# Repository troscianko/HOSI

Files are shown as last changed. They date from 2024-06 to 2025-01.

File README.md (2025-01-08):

# HOSI: Hyperspectral open source imager

_Developed by Jolyon Troscianko_

The hyperspectral open-source imaging system (HOSI) is an innovative and low-cost solution for collecting full-field hyperspectral data. The system uses a Hamamatsu C12880MA micro spectrometer to take single-point measurements, together with a motorised gimbal for spatial control. The hardware uses off-the-shelf components and 3D printed parts, costing around £350 in total. The system can run directly from a computer or smartphone with a graphical user interface, making it highly portable and user-friendly.

The HOSI system can take panoramic hyperspectral images that meet the difficult requirements of ALAN research, sensitive to low light around 0.001 cd.m-2, across 320-880nm range with spectral resolution of ~9nm (FWHM) and spatial resolution of ~0.2 degrees. The independent exposure of each pixel also allows for an extremely wide dynamic range that can encompass typical natural and artificially illuminated scenes, with sample night-time scans achieving peak-to-peak dynamic ranges of >50,000:1.

This system's adaptability, cost-effectiveness, and open-source nature position it as a valuable tool for researchers investigating the complex relationships between light, environment, behaviour, ecology, and biodiversity, with further potential uses in many other fields.

# Publicaiton:
For further information, including detailed performance data, see my paper:

**Troscianko, J.** A hyperspectral open-source imager (HOSI). _BMC Biol_ 23, 5 (2025). https://doi.org/10.1186/s12915-024-02110-w

Please cite the above paper if you use this project :)

# Videos:
Intro video (https://www.youtube.com/watch?v=9q8lyUpntms)
Assembly video (https://www.youtube.com/watch?v=4VSr_2GacWA)
Firmware video (https://www.youtube.com/watch?v=N6yWZMLm-1M)
Calibration video (https://www.youtube.com/watch?v=MEW3B65dHIc)
Imaging video (https://www.youtube.com/watch?v=LO7XNOPuY0w)

# Figures:

wiring and 3D parts
_Figure 1. 3D parts and wiring. a) Photograph of a HOSI unit in the field, running from a smartphone. b): 3D assembly; c): parts arranged for 3D printing; d): wiring diagram and required wire lengths. GND (ground) is the shared negative voltage, VIN is the 5v output from the Arduino that is delivered via the USB cable. Note that the spectrometer should be connected to the Arduino’s regulated 5v output (as shown), not VIN that has a slightly lower voltage due to a protective diode in the Arduino._

GUI2
_Figure 2. Graphical user interface (GUI) layout, showing the available functions and a scan of butterflies. The spectrum shows a selection from a patch of wing that appears black to human vision, but has a UV peak visible to many other animals. This scene was illuminated by an Exo-Terra Sunray lamp._


_Figure 3. Example hyperspectral scan of Falmouth (UK) docks at night. a): panoramic photograph of the scene; b): HOSI’s hyperspectral RGB preview image; c): radiance plots created by the HOSI GUI at chosen pixels (x-axis: wavelength [nm]; y-axis: linear radiance Le [W.sr-1.m-2.nm-1]). These spectra illustrate how individual light sources can be identified and compared. The highest spectral peak in the brightest pixel of this hyperspectral image is approximately 50,000 times higher than the peak in the darkest pixel. The full dynamic range (highest peak to lowest trough) is considerably greater, and can be maximised further with longer exposure times to reduce noise._

**Description of HOSI file output format** (each scan generates a .csv file and .png image):
_First line:_

'h' denotes start of raw data from HOSI, unit #, pan left limit, pan right limit, pan resolution steps-per-scan, tilt lower limit, tilt upper limit, tilt resolution (steps-per-scan), maximum integration time (microseconds), boxcar spectral pooling value, delay between dark measurement repeats (milliseconds)

_Second line onwards:_

pan location (steps), tilt location (steps), measurement type (0=dark measurement, 1=light measurement, 2=initialisation exposure), integration time (microseconds), number of wavelength bins reaching saturation point, spectral count data (288 comma-delineated measurements unless a boxcar>1 is used)

'x' denotes end of raw data

Following this, a table of processed, calibrated _Le_ values are shown, together with wavelengths, and pan/tilt locations. Note that this table uses the calibration data present when the raw file was generated.

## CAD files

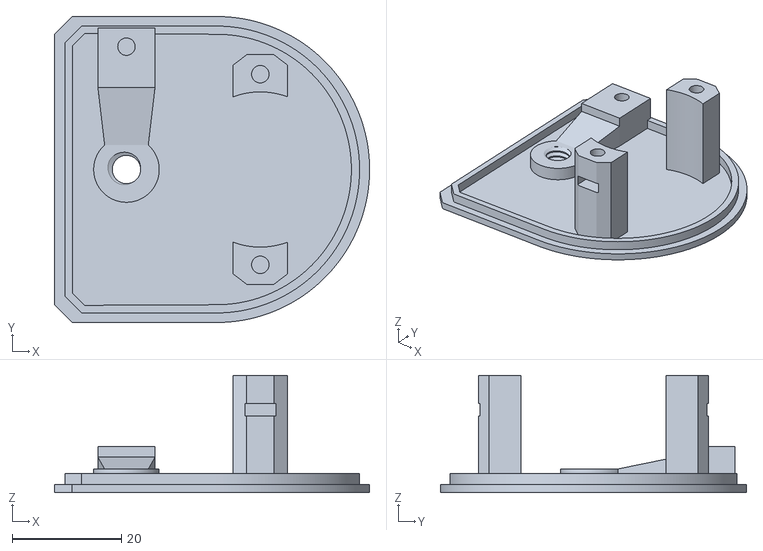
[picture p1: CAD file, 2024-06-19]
3D Models/Base B.stl
57.7 x 56.0 x 21.5

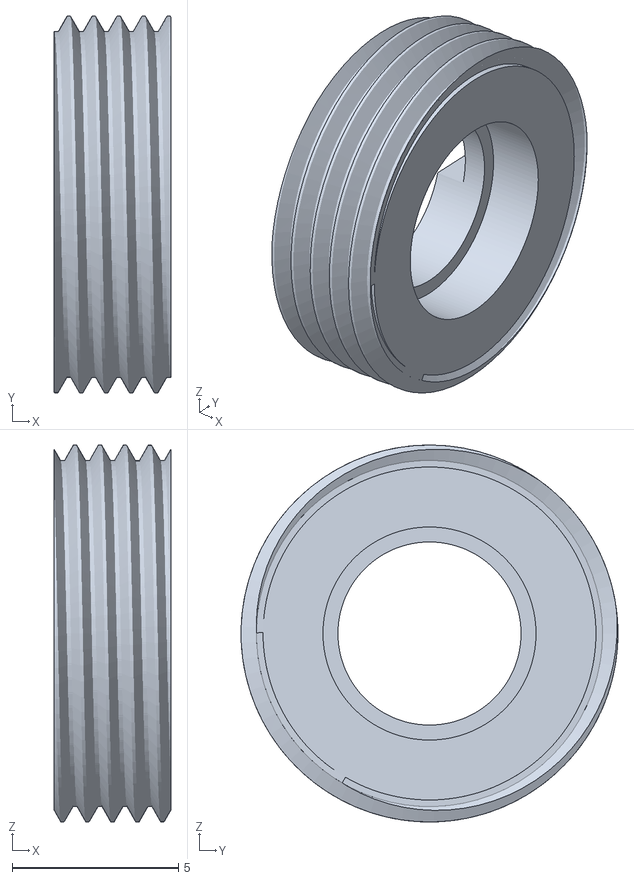
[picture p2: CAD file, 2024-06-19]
3D Models/Lens holder.stl
3.50 x 11.3 x 11.3

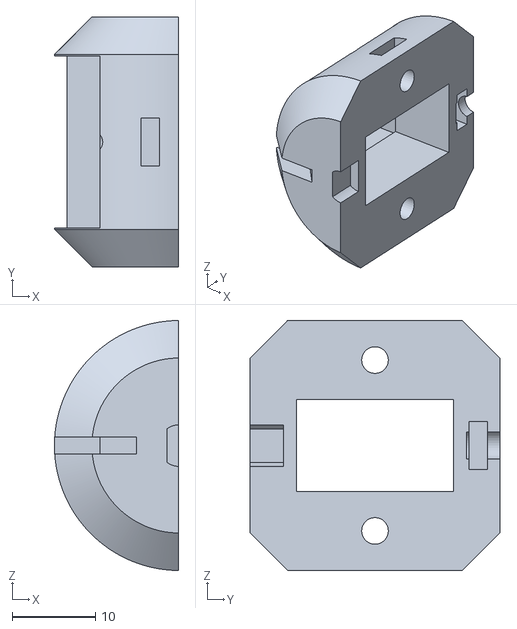
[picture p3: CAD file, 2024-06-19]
3D Models/Tilt B.stl
14.9 x 30.0 x 30.0

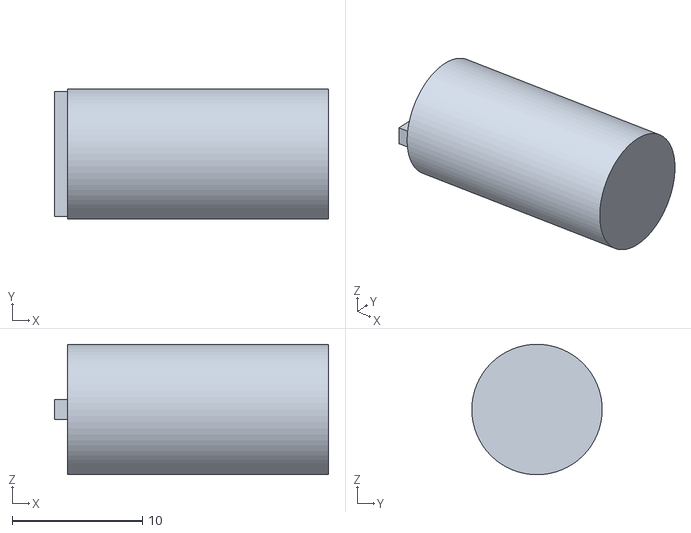
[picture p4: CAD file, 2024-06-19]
3D Models/Focus tool.stl
21.0 x 10.0 x 10.0

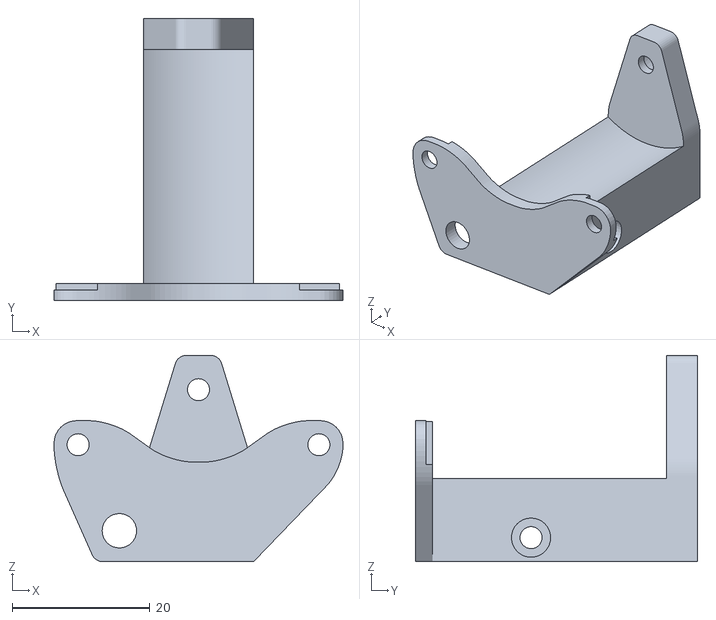
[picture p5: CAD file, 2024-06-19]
3D Models/Pan bracket.stl
42.0 x 41.0 x 30.0

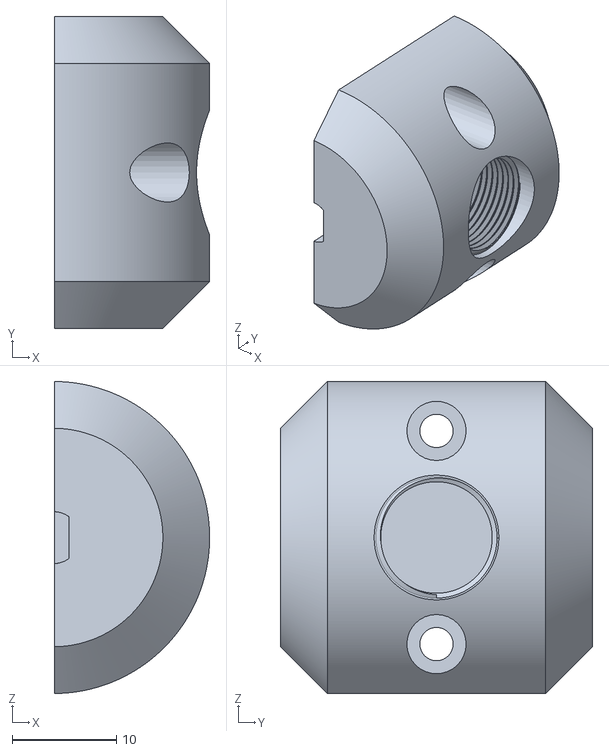
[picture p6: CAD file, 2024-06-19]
3D Models/Tilt A.stl
14.9 x 30.0 x 30.0

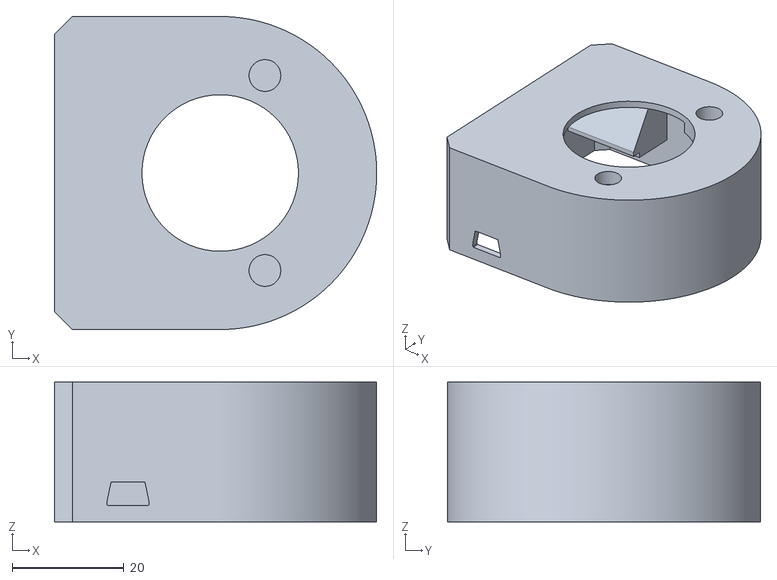
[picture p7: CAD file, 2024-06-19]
3D Models/Base A.stl
57.7 x 56.0 x 25.0

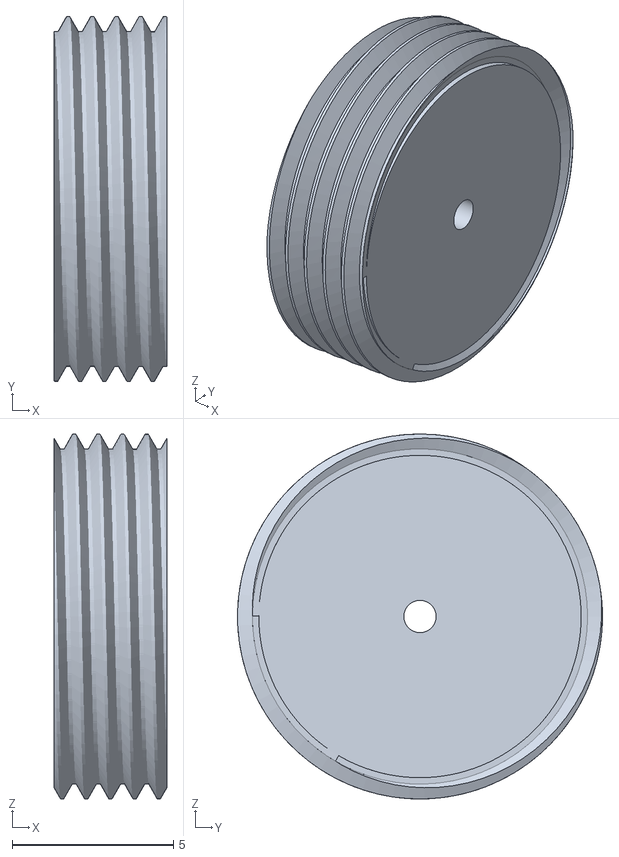
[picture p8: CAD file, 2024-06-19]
3D Models/Light reducer 1mm.stl
3.50 x 11.3 x 11.3

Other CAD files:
3D Models/Light reducer 2mm.stl

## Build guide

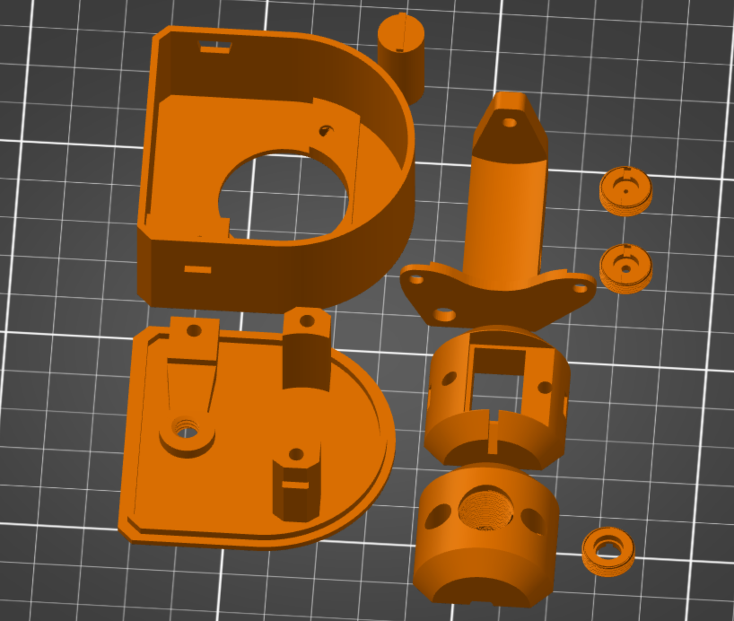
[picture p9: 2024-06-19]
3D Models/Print orientations.png

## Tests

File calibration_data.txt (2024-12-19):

unit,data,
9,wavCoef,3.150073901E+02,2.700335692E+00,-1.370721454E-03,-5.494487172E-06,1.475143134E-09,1.441646208E-11,
9,radSens,10.57054,10.31393,9.96353,9.75570,9.90073,10.52882,11.67749,13.29625,15.25959,17.38610,19.46953,21.31691,22.78413,23.79880,24.36451,24.54783,24.45461,24.20453,23.90981,23.66150,23.52308,23.53039,23.69609,24.01660,24.47917,25.06546,25.75057,26.49864,27.25994,27.97367,28.57747,29.02001,29.27114,29.32534,29.19893,28.92344,28.53918,28.08971,27.61815,27.16415,26.76176,26.43859,26.21611,26.11092,26.13597,26.30099,26.61160,27.06730,27.66013,28.37490,29.19203,30.09118,31.05243,32.05223,33.05475,34.00388,34.82338,35.42944,35.75312,35.76313,35.47760,34.95881,34.29317,33.56562,32.83927,32.14679,31.49384,30.87027,30.26316,29.66717,29.08916,28.54665,28.06171,27.65326,27.33167,27.09737,26.94303,26.85745,26.82873,26.84534,26.89544,26.96527,27.03859,27.09778,27.12658,27.11312,27.05206,26.94520,26.80059,26.63053,26.44892,26.26822,26.09717,25.93981,25.79622,25.66434,25.54181,25.42684,25.31836,25.21585,25.11898,25.02774,24.94233,24.86304,24.78973,24.72115,24.65448,24.58571,24.51068,24.42651,24.33254,24.23028,24.12271,24.01346,23.90639,23.80552,23.71480,23.63732,23.57414,23.52325,23.47947,23.43524,23.38199,23.31145,23.21658,23.09247,22.93664,22.74920,22.53245,22.29057,22.02964,21.75775,21.48440,21.21869,20.96663,20.72914,20.50203,20.27826,20.05127,19.81782,19.57902,19.33942,19.10503,18.88135,18.67205,18.47842,18.29935,18.13191,17.97274,17.81980,17.67365,17.53706,17.41271,17.30013,17.19391,17.08403,16.95850,16.80697,16.62389,16.41045,16.17463,15.92983,15.69204,15.47680,15.29626,15.15735,15.06100,15.00240,14.97182,14.95597,14.93989,14.90964,14.85537,14.77440,14.67273,14.56386,14.46429,14.38725,14.33748,14.30931,14.28929,14.26120,14.21113,14.13064,14.01787,13.87669,13.71445,13.53934,13.35800,13.17552,12.99744,12.83223,12.69203,12.59003,12.53552,12.52887,12.55890,12.60349,12.63355,12.61860,12.53263,12.35920,12.09501,11.75136,11.35251,10.93063,10.51851,10.14253,9.81825,9.54977,9.33226,9.15557,9.00737,8.87521,8.74718,8.61231,8.46099,8.28568,8.08207,7.84967,7.59159,7.31309,7.01973,6.71651,6.40891,6.10583,5.82341,5.58792,5.43539,5.40608,5.53381,5.83285,6.28837,6.85490,7.46404,8.03821,8.50524,8.80975,8.91932,8.82560,8.54190,8.09844,7.53661,6.90294,6.24326,5.59761,4.99634,4.45827,3.99102,3.59353,3.25990,2.98304,2.75728,2.57912,2.44651,2.35739,2.30877,2.29604,2.31302,2.35209,2.40473,2.46246,2.51802,2.56604,2.60216,2.62187,2.61994,2.59173,2.53572,2.45605,2.36296,2.27099,2.19597,2.15221,2.15024,2.19468,2.28250,2.40223,2.53538,2.65999,2.75539,2.80680,2.80867,2.76586,2.69257,2.60923,2.53784,2.49689,
9,linCoefs,0.91106809,0.58315014,

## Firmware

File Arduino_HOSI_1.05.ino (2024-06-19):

/*

_________________________HOSI Arduino Firmware_____________________________

 Written by: Jolyon Troscianko
 initial release: 19/06/2024
 License: GNU General Public License v3.0
 
 
 Manual control:
 The HOSI can be controlled automatically by the HOSI_GUI Python software. however, the functions can
 also be accessed manually via a serial port (check the baud, default 115200)
 
 tilt: send "l" followed by a number e.g. "l100" or "l500" note that zero is straight down, do not use negative values
 pan: send "p" followed by a number e.g. "p100" or "p-1000" note that zero is straight ahead
 manual integration time: send "t" followed by microsecond number
 radiance measurement: send "r" and it will take a radiance measurement
 hyperspectral measurement: send "h" followed by comma-delineated values as follows:
 panLeft,panRight,panResolution,tiltBottom,tiltTop,tiltResolution,maxIntegrationTime(microseconds),boxcar,darkRepeatTimer(milliseconds)
 e.g.: "h-200,200,10,400,600,10,2000000,2,120000"
  
 
 Modify the unit number below if desired, and upload this script to an Arduino Nano or similar.
 
 
 */


#include <AccelStepper.h>




int unitNumber = 9; // Change this number to whatever you want, and link this to the calibration data in calibration_data.txt


#define TRGpin A0
#define STpin A1
#define CLKpin A2
#define VIDEOpin A3

#define nSites 288 // 
uint16_t data[nSites] [2];
int dataLoc = 0;

int delayTime = 1;
long intTime = 100;
long prevIntTime = 100;
long maxIntTime = 3000000; // maximum integration time for auto & manual measurement milliseconds
int minIntTime = 50; //the sensor doesn't work below a certain numebr of scans... it needs three cycles with the ST pin high, even then you need to add about 378 microseconds to the exposure
int intStep = 400;
long manIntTime = 0;
int satN = 0; // number of bands over-exposed
int prevSatN = 0;
int satVal = 998; // over-exposure value

// used to control the reduction of redundant measurements at high elevations
int panoSteps[] = {913, 959, 988, 1005};
int panoSpaces[] = {2, 4, 8, 16};

long hyperVals[9];
long panVal = 0;
long tiltVal = 0;
int darkLight = 1; // 0= dark measurement, 1=light measurement
long darkRepeat = 30000;// repeat dark measurement every few seconds/minutes

AccelStepper stepper_pan(4, 3, 5, 2, 4); // 8=HALF4WIRE, then input pin 1, 2, 3, 4
AccelStepper stepper_tilt(4, 7, 9, 6, 8); // 8=HALF4WIRE, then input pin 1, 2, 3, 4

int boxcar = 1;



void setup() {
  stepper_pan.setMaxSpeed(500.0); // 800 for half-step
  stepper_pan.setAcceleration(5000.0);
  stepper_pan.disableOutputs();

  stepper_tilt.setMaxSpeed(500.0);
  stepper_tilt.setAcceleration(5000.0);  
  stepper_tilt.disableOutputs();
      
  //Set desired pins to OUTPUT
  pinMode(CLKpin, OUTPUT);
  pinMode(STpin, OUTPUT);

  digitalWrite(CLKpin, HIGH);
  digitalWrite(STpin, LOW);

  Serial.begin(115200); // Baud Rate set to 115200, 500000 seems to work well for nano with PC, 230400 and 256000 doesn't work for android. interestingly it still works ok with 57600
  while (! Serial); // Wait untilSerial is ready
  readSpectrometer();
  resetData();
  
}




void readSpectrometer(){

  // Start clock cycle and set start pulse to signal start
  digitalWrite(CLKpin, LOW);
  delayMicroseconds(delayTime);
  digitalWrite(CLKpin, HIGH);
  delayMicroseconds(delayTime);
  digitalWrite(CLKpin, LOW);
  digitalWrite(STpin, HIGH);
  delayMicroseconds(delayTime);

  // microseconds
     unsigned long cTime = micros(); // start time
     unsigned long eTime = cTime + intTime; // end time
  
  //Sample for a period of time
 // for(int i = 0; i < 15; i++){ //orig 15
     while(cTime < eTime){
         digitalWrite(CLKpin, HIGH);
         delayMicroseconds(delayTime);
         digitalWrite(CLKpin, LOW);
         delayMicroseconds(delayTime);
         cTime=micros();
      } 

  //Set STpin to low
  digitalWrite(STpin, LOW);

  //Sample for a period of time
  for(int i = 0; i < 88; i++){ //87 aligns correctly

      digitalWrite(CLKpin, HIGH);
      delayMicroseconds(delayTime);
      digitalWrite(CLKpin, LOW);
      delayMicroseconds(delayTime); 
      
  }

  int specRead = 0;
  satN = 0;
  for(int i = 0; i < nSites; i++){

      specRead = analogRead(VIDEOpin);
      // second read shoudl stablise the multiplexer and give more accurate read
      //delayMicroseconds(delayTime);
     // specRead = analogRead(VIDEOpin);
      data[i][dataLoc] += specRead;
      if(specRead > satVal)
        satN ++;
      
      digitalWrite(CLKpin, HIGH);
      delayMicroseconds(delayTime);
      digitalWrite(CLKpin, LOW);
      delayMicroseconds(delayTime);
        
  } 
}



void resetData(){
  for (int i = 0; i < nSites; i++)
    data[i][dataLoc] = 0;
}

void switchDim(){
  if(dataLoc == 0)
    dataLoc = 1;
  else
    dataLoc = 0;
}

void radianceMeasure(){

  // reset all data
  dataLoc = 1;
  resetData();
  dataLoc = 0;
  resetData();

  // ----------------- AUTO EXPOSURE-----------
  if(manIntTime == 0){ 
    intTime = minIntTime; // microsecond exposure
    readSpectrometer(); // read to dim0
    //data[0][dataLoc] = -1; // debugging
    prevSatN = satN;
    prevIntTime = intTime;
    intTime = intStep;
    if(satN > 0)
      switchDim(); // required if first exposure is over-exposed

    while(satN == 0 && intTime < maxIntTime){
      switchDim();
      resetData();
      readSpectrometer();
      //data[0][dataLoc] = intTime;// debugging

      if(satN == 0){
        prevSatN = satN;
        prevIntTime = intTime;
        intTime = intTime*2;
      }

    } //while

    //if(prevIntTime > -1) // if first exposure isn't over-exposed
      switchDim(); 
      
  //------------- MANUAL EXPOSURE-------------
  } else { 
    intTime = manIntTime;
    readSpectrometer(); // read to dim0
    prevSatN = satN;
    prevIntTime = intTime;
  }
 
  Serial.print(String(panVal) + "," + String(tiltVal) + "," + String(darkLight) + "," + String(prevIntTime) + "," + String(prevSatN) );

  for (int i = 0; i < nSites; i+=boxcar){
    int tSum = 0;
    for(int j = 0; j < boxcar; j++)
      if(i+j <= nSites)
          tSum += data[i+j][dataLoc];
    Serial.print("," + String(tSum));
  }
  Serial.print("\n");
  delay(1);
 
}


void pan(long pv){
  //stepper_pan.enableOutputs();
  stepper_pan.runToNewPosition(pv);
  //stepper_pan.disableOutputs();
}

void tilt(long tv){
  //stepper_tilt.enableOutputs();
  stepper_tilt.runToNewPosition(tv);
  //stepper_tilt.disableOutputs();
}

void darkMeasure(){
      //-----------Return to zero point------------
      //panVal = 0;
      //pan(0);
      //tiltVal = 0;
      tilt(0);
      darkLight = 0; // dark measurement
      long tl = manIntTime; // save existing manual value

      // first scan at microsecond
      manIntTime = minIntTime;
      radianceMeasure();
   
      for (long i = intStep; i <= maxIntTime; i*= 2){
        manIntTime = i;
        radianceMeasure();
      }

      manIntTime = tl;// restore manIntTime
      darkLight = 1; // light measurement
}

void startMeasure(){
      //-----------Return to zero point------------
      //panVal = 0;
      pan(0);
      //tiltVal = 512;
      tilt(512);
      darkLight = 2; // dark measurement
      radianceMeasure();
      darkLight = 1; // light measurement
}


void loop() {

  
  String arg = Serial.readString();

  if (arg != NULL){

    // manually set integration time
    if(arg.startsWith("t") == true){
      arg.replace("t", "");
      manIntTime = (long) arg.toFloat();
      if(manIntTime > maxIntTime)
          manIntTime = maxIntTime;
      Serial.println("int. time: " + String(manIntTime) + "ms");

    // manual pan
    } else if(arg.startsWith("p") == true){
      arg.replace("p", "");
      stepper_pan.enableOutputs();
      pan((int) arg.toFloat());
      stepper_pan.disableOutputs();
      Serial.println("pan: " + String((int) arg.toFloat()));
      delay(5);

    // manual tilt
    } else if(arg.startsWith("l") == true){
      arg.replace("l", "");
      stepper_tilt.enableOutputs();
      tilt((int) arg.toFloat());
      stepper_tilt.disableOutputs();
      Serial.println("tilt: " + String((int) arg.toFloat()));
      delay(5);

    // Manual spec measure
    } else if(arg.startsWith("r") == true){ // radiance

      radianceMeasure();

    // -------------  hyperspec --------------
    } else if(arg.startsWith("h") == true){
      arg.replace("h", "");
      int i= 0;
      while(arg.indexOf(",") != -1){
        hyperVals[i] = long(arg.substring(0,arg.indexOf(",")).toFloat()); //toInt for int, atol for long
        i++;
        arg = arg.substring(arg.indexOf(",")+1);
      }

   

      Serial.println("h," + String(unitNumber) + "," + String(hyperVals[0]) + "," + String(hyperVals[1]) + "," + String(hyperVals[2]) + "," + String(hyperVals[3]) + "," + String(hyperVals[4]) + "," + String(hyperVals[5]) + "," + String(hyperVals[6]) + "," + String(hyperVals[7]) + "," + String(hyperVals[8]) );
      delay(5);
      //arg = Serial.readString();
      
      maxIntTime = (long) hyperVals[6];
      boxcar = (int) hyperVals[7];
      darkRepeat = (long) hyperVals[8];

      stepper_pan.enableOutputs();
      stepper_tilt.enableOutputs();
      //panVal = 0;
      pan(0);
      tilt(0);

      //-----------Dark Measure at start------------
      startMeasure();
      darkMeasure();

      unsigned long cDR = millis(); // current time dark repeat
      unsigned long eDR = cDR + darkRepeat; // end time dark repeat
      
      for(tiltVal = hyperVals[3]; tiltVal <= hyperVals[4]; tiltVal += hyperVals[5]){
        
        //----------repeat dark measurement based on timeout-----------
        cDR = millis();
        if(cDR >= eDR){
            darkMeasure();
            //tilt(tiltVal);
            cDR = millis();
            eDR = cDR + darkRepeat;
        }

        tilt(tiltVal);
        pan(hyperVals[0]-10);// overshoot - pan left a bit to use up excess in gears

        //--------reduce measurement frequency at high elevations
        int panShift = 1;
        int panStart = 0;
        for(int i=0; i<4; i++)
        if(tiltVal >= panoSteps[i]){
            panShift = panoSpaces[i];
            panStart = panoSpaces[i]/2;
        }
        panShift *= hyperVals[2];
        panStart *= hyperVals[2];
            
        /*
        if(panVal >= hyperVals[1]){
          //----------pan from right to left-----------
          for(panVal = hyperVals[1]-panStart; panVal >= hyperVals[0]; panVal -= panShift){ 
            pan(panVal);
            radianceMeasure();
          }
        } else {
        */
          //----------pan from left to right-----------
          for(panVal = hyperVals[0]+panStart; panVal <= hyperVals[1]; panVal += panShift){ 
            pan(panVal);
            radianceMeasure();
          }
        //}

      }


      //-----------Dark Measure at end------------
      pan(0);
      darkMeasure();

      stepper_pan.disableOutputs();
      stepper_tilt.disableOutputs();

      Serial.println("x"); // signal end
//      Serial.println("\n"); // signal end
    }
  }

  delay(10);  
     
  


}
